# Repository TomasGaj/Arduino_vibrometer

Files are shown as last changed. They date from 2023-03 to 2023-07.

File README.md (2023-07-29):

# Arduino UNO contactless vibrometer

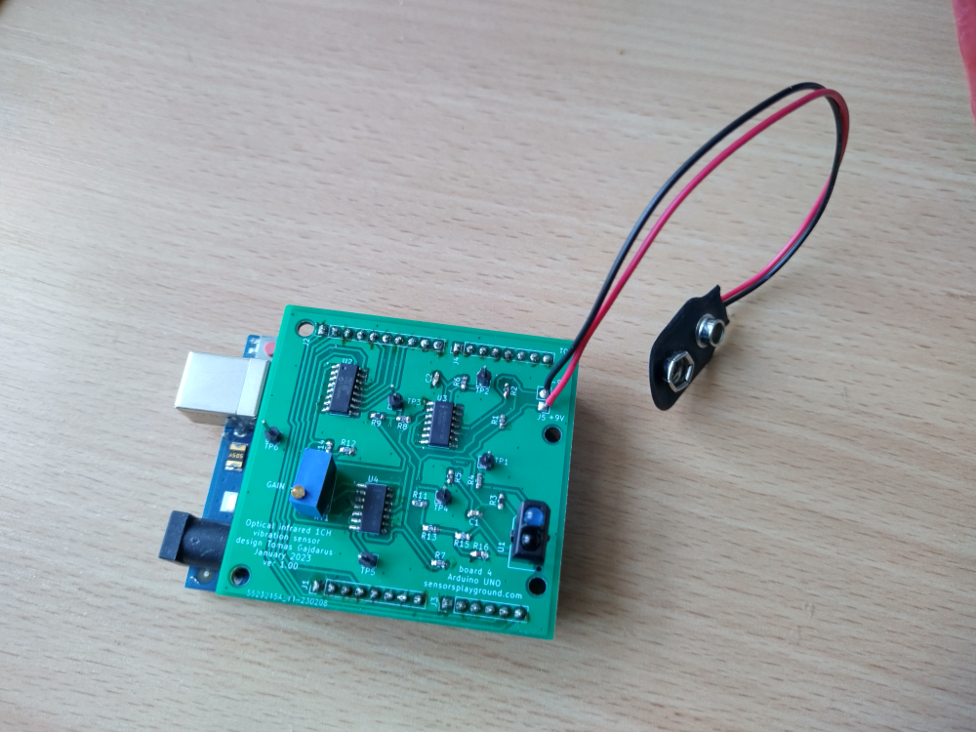
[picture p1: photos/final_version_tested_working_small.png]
final_version_tested_working_small


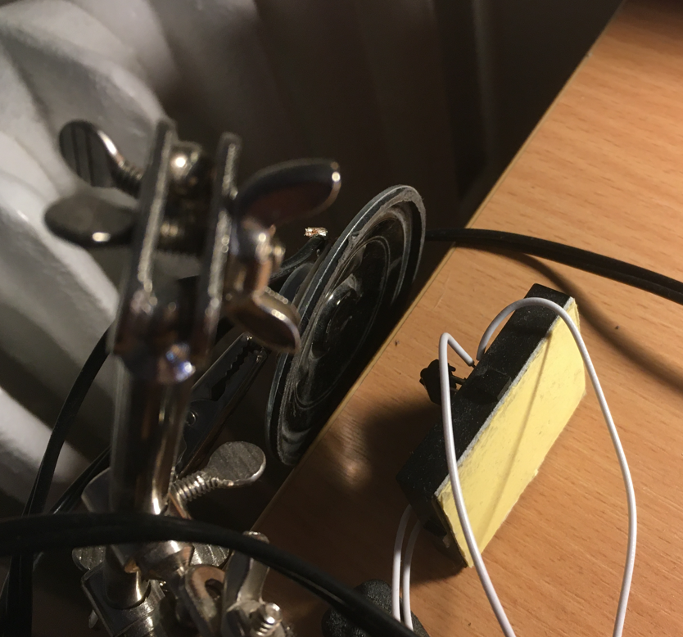
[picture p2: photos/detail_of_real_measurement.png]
detail of real measurement


**UPDATE 29-07-2023: I've squized Arduino and MPC3008 to the maximum, in the meanwhile
I didn't continue in C# as I optimized Arduino otput data format, see:** [Arduino_Nano_MPC3008_logger](https://github.com/TomasGaj/Arduino_Nano_MPC3008_logger)

## General Introduction

It's expansion board for Arduino UNO.
Vibrometer is based on TCRT5000 IR sensor and MCP3008 adc.
I used KiCAD 6.0.
It's tested and working.
Arduino is used only to send out ADC values together with time stamps.
C# application is coming.
Up to now I was not able to eliminate noise comping from USB supply (50 Hz), so I use 9V battery to supply power to the circuit.

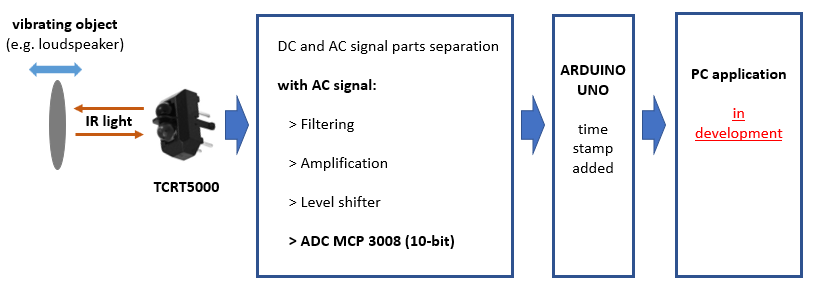
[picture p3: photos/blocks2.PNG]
blocks


## Physical principle

It's light intensity distance sensor. The closer the object is, the more light is reflected back to phototransistor.
However, the correct distance of vibrating object can not be measured without calibration. I hope I'll solve later.
Working distance is 15-25 mm.

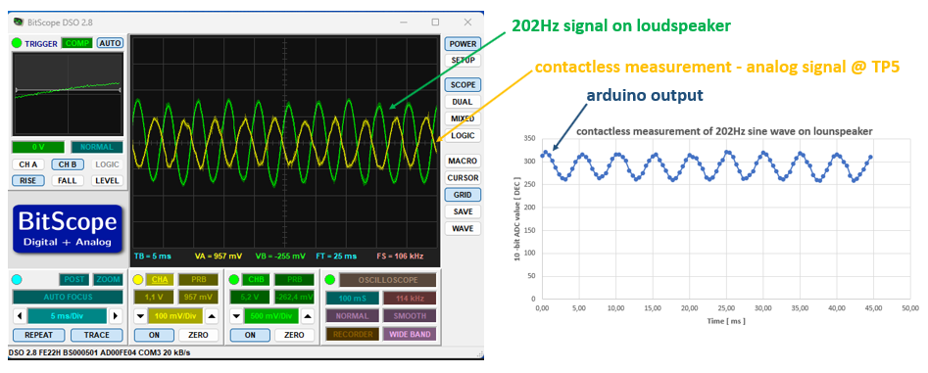
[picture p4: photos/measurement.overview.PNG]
measurement.overview


## Arduino code

I use this SW library:
[Fast MCP3008 library for Arduino Uno](https://github.com/arithmechanics/fast-MCP3008)

I modified the original code, I am sending out data in this format:

**ADC VALUE** (hex, 10-bit adc) ***(space)*** **MICRO-SECONDS** (hex, result of Arduino function ***micros()***)

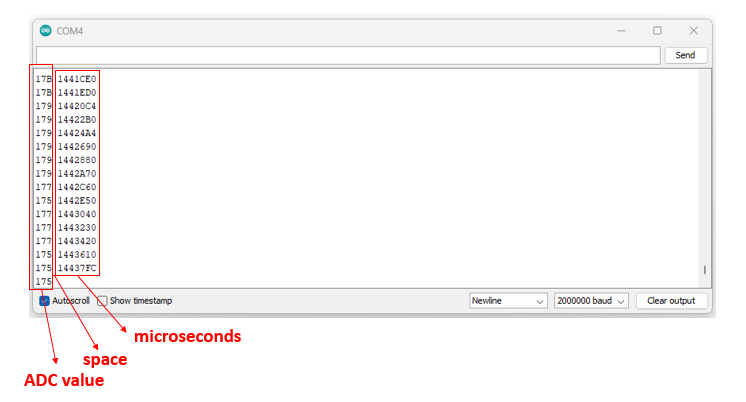
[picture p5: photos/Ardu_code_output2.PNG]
Arduino code output


## Electrical circuit
**Signal path:**

Signal -> High pass filter -> Low pass filter -> Amplifier -> Level shifter -> ADC (here MCP3008) -> Arduino Uno

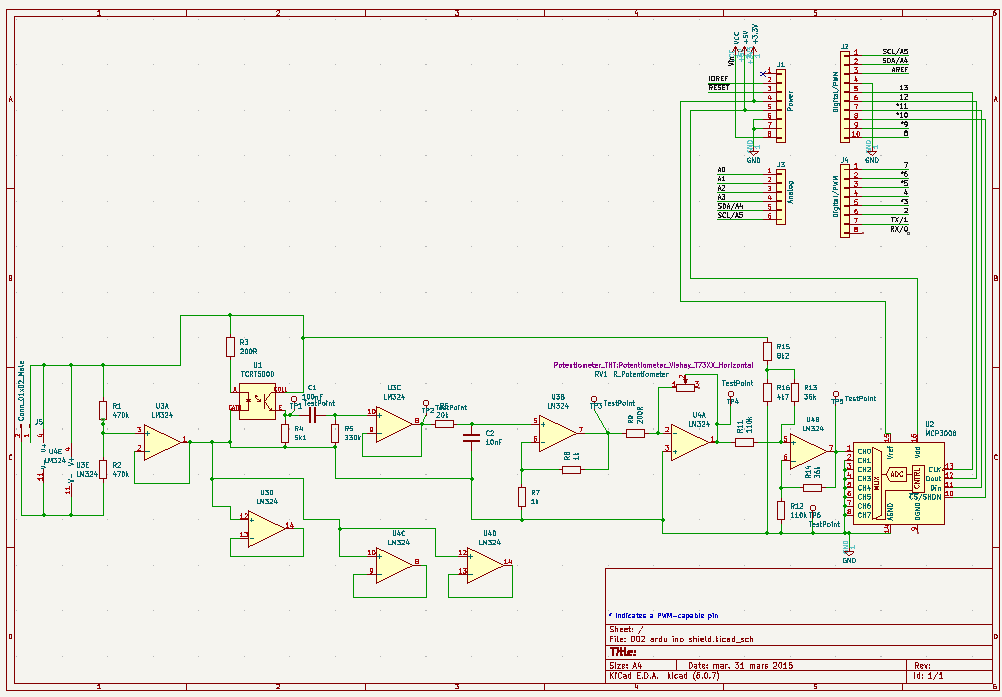
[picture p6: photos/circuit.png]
circuit


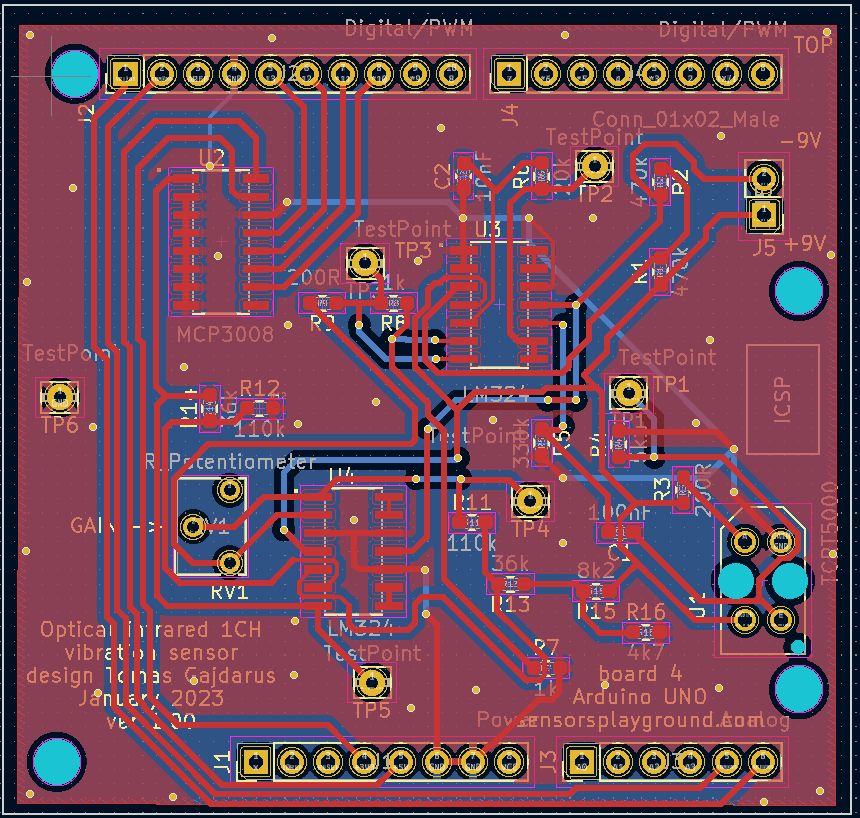
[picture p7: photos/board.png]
board


**My electrical design is inspired by:**

[Matiss Malahs - Design of a Low Cost Laser Vibrometer System](https://www.theseus.fi/handle/10024/89919)

[Heart Rate Measurement using PPG](http://www.ee.iitb.ac.in/~stallur/wp-content/uploads/2017/02/Heart-Rate-Measurement-using-PPG1.pdf)

## Details of the electrical circuit
I needed to do adjustments:
   - high pass filter is calculater fc = 4.82 Hz
   - high pass is also removing away DC part of the signal
   - low pass is calculated fc = 796 Hz
   - **everythnig above 200Hz looks ugly with actual data acqusition speed**
   - TestPoint 1 - direct output from phototransistor (proportional to light intensity)
   - TestPoint 2 - voltage after high pass filter
   - TestPoint 3 - voltage after low pass filter
   - TestPoint 4 - voltage after amplification
   - TestPoint 5 - signal before entering ADC
   - TestPoint 6 - ground
   
## Next steps

  - testing and testing...
  - speed up Arduino code
  - eliminate 9V battery
  - finish C# app
  - thinking about ARM processor (now testing RPi)
  - thinking about more complicated physical principle (planning intensity modulation tests, reading about self-mixing)
 
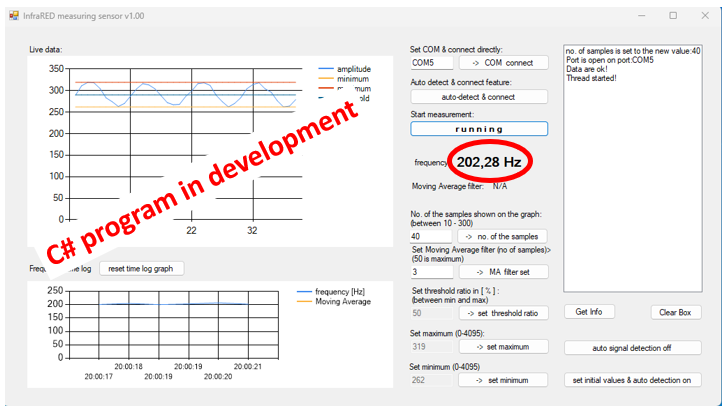
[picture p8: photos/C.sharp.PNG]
C#
 
 
**More about testing and other details:**

[sensorsplayground.com](http://www.sensorsplayground.com/)

Enjoy!

Tomas Gajdarus

tomas (dot) gajdarus (at) seznam (dot) cz

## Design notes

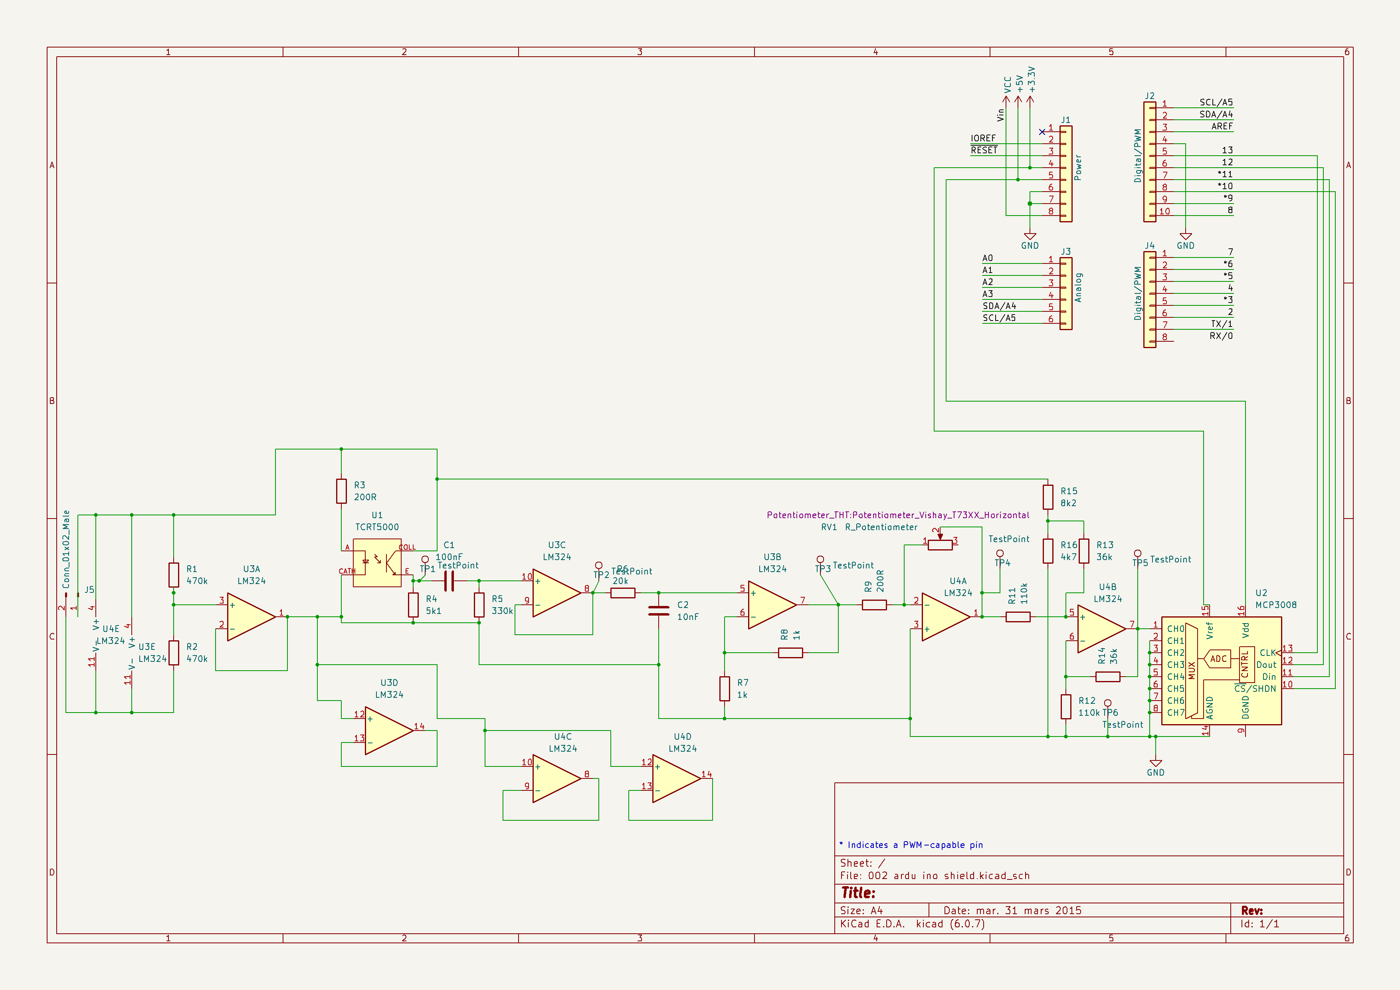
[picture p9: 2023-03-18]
Schematics and 3D view v1.0/Arduino_vibrometer_schematics_v 1.0.png

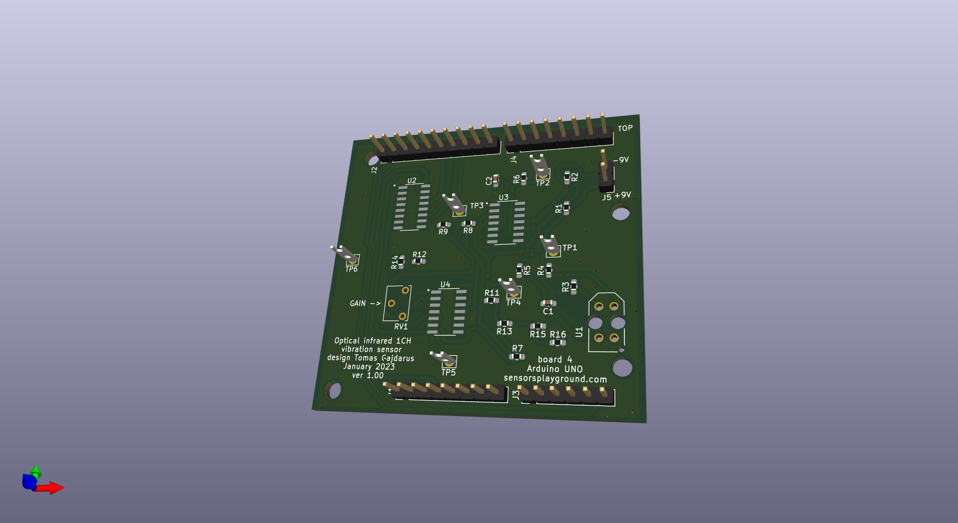
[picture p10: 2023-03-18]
Schematics and 3D view v1.0/3D_view_v1.0.jpg

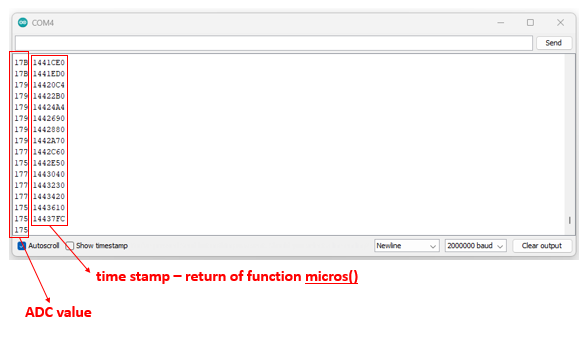
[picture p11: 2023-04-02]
photos/Ardu_code_output.PNG

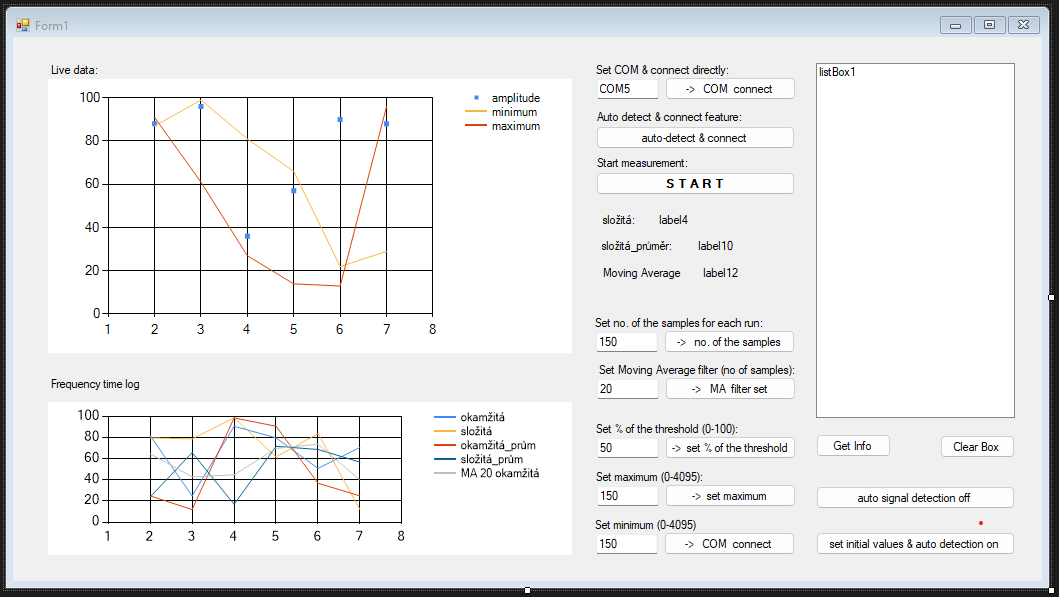
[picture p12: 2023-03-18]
photos/C# PC application (in development).png

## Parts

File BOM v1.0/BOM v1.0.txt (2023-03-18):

18.3.2023

created by Tomas Gajdarus

Note:in BOM is missing (I had components in-house):

	- 20k potenciometer
	- TCRT5000
	- 9V battery connector

FARNELL

1x MCP3008-I/SL 10BIT ADC, 8 CH, SPI, SMD, SOIC16
Order Code: 1292241 

2x LM324ADR OP AMP, QUAD LOW POWER, SMD, SOIC14
Order Code: 3117046

2x RC0603FR-07470KL RES, 470K, 1%, 0.1W, 0603, THICK FILM
Order Code: 9238808

2x CRCW0603200RFKEA RES, 200R, 1%, 0.1W, 0603, THICK FILM
Order Code: 1469777

1x MCWR06X5101FTL RES, 5K1, 1%, 0.1W, 0603, THICK FILM
Order Code: 2447404

1x CR0603-FX-3303ELF RES, 330K, 1%, 0603, THICK FILM
Order Code: 2908296 

1x RC0603FR-0720KL RES, 20K, 1%, 0.1W, 0603, THICK FILM
Order Code: 3495765

2x MCWR06X1001FTL RES, 1K, 1%, 0.1W, 0603, THICK FILM
Order Code: 2447272 

1x RC0603FR-0736KL RES, 36K, 1%, 0.1W, 0603, THICK FILM
Order Code: 3495824

1x MCWR06X8201FTL RES, 8K2, 1%, 0.1W, THICK FILM
Order Code: 2447442 

1x SFR03EZPF4701 RES, 4K7, 1%, 0603, THICK FILM
Order Code: 2887235

2x MCWR06X1103FTL RES, 110K, 1%, 0.1W, THICK FILM
Order Code: 2447234

1x 0603YC103KAT2A CAP, 0.01µF, 16V, 10%, X7R, 0603
Order Code: 2280661

1x 0603YC104JAT2A CAP, 0.1µF, 16V, 5%, X7R, 0603
Order Code: 1740612 

2x 2211S-22G CONNECTOR, HEADER, 22POS, 1ROW, 2.54MM
Order Code: 2847167

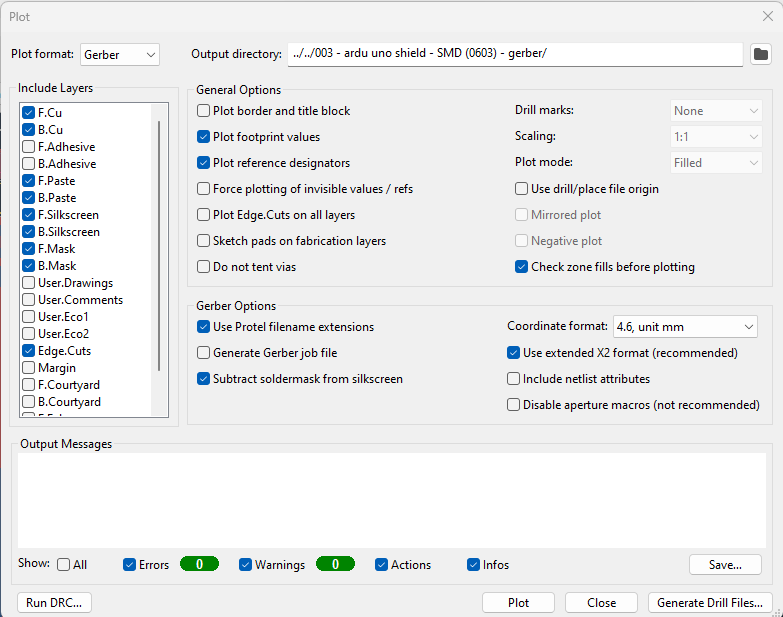
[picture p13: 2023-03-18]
Gerber files (ordered in JLCPCB, tested, working)/jak KiCAD 2023-02-08 082753.png

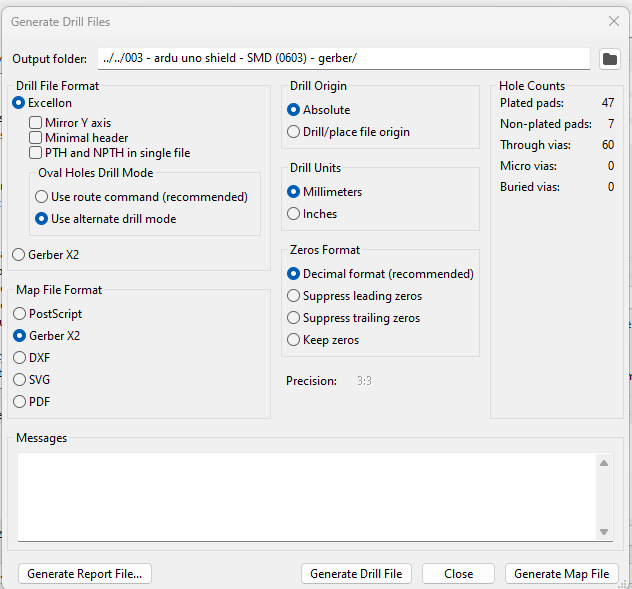
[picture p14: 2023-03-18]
Gerber files (ordered in JLCPCB, tested, working)/jak KiCAD2 2023-02-08 082753.png

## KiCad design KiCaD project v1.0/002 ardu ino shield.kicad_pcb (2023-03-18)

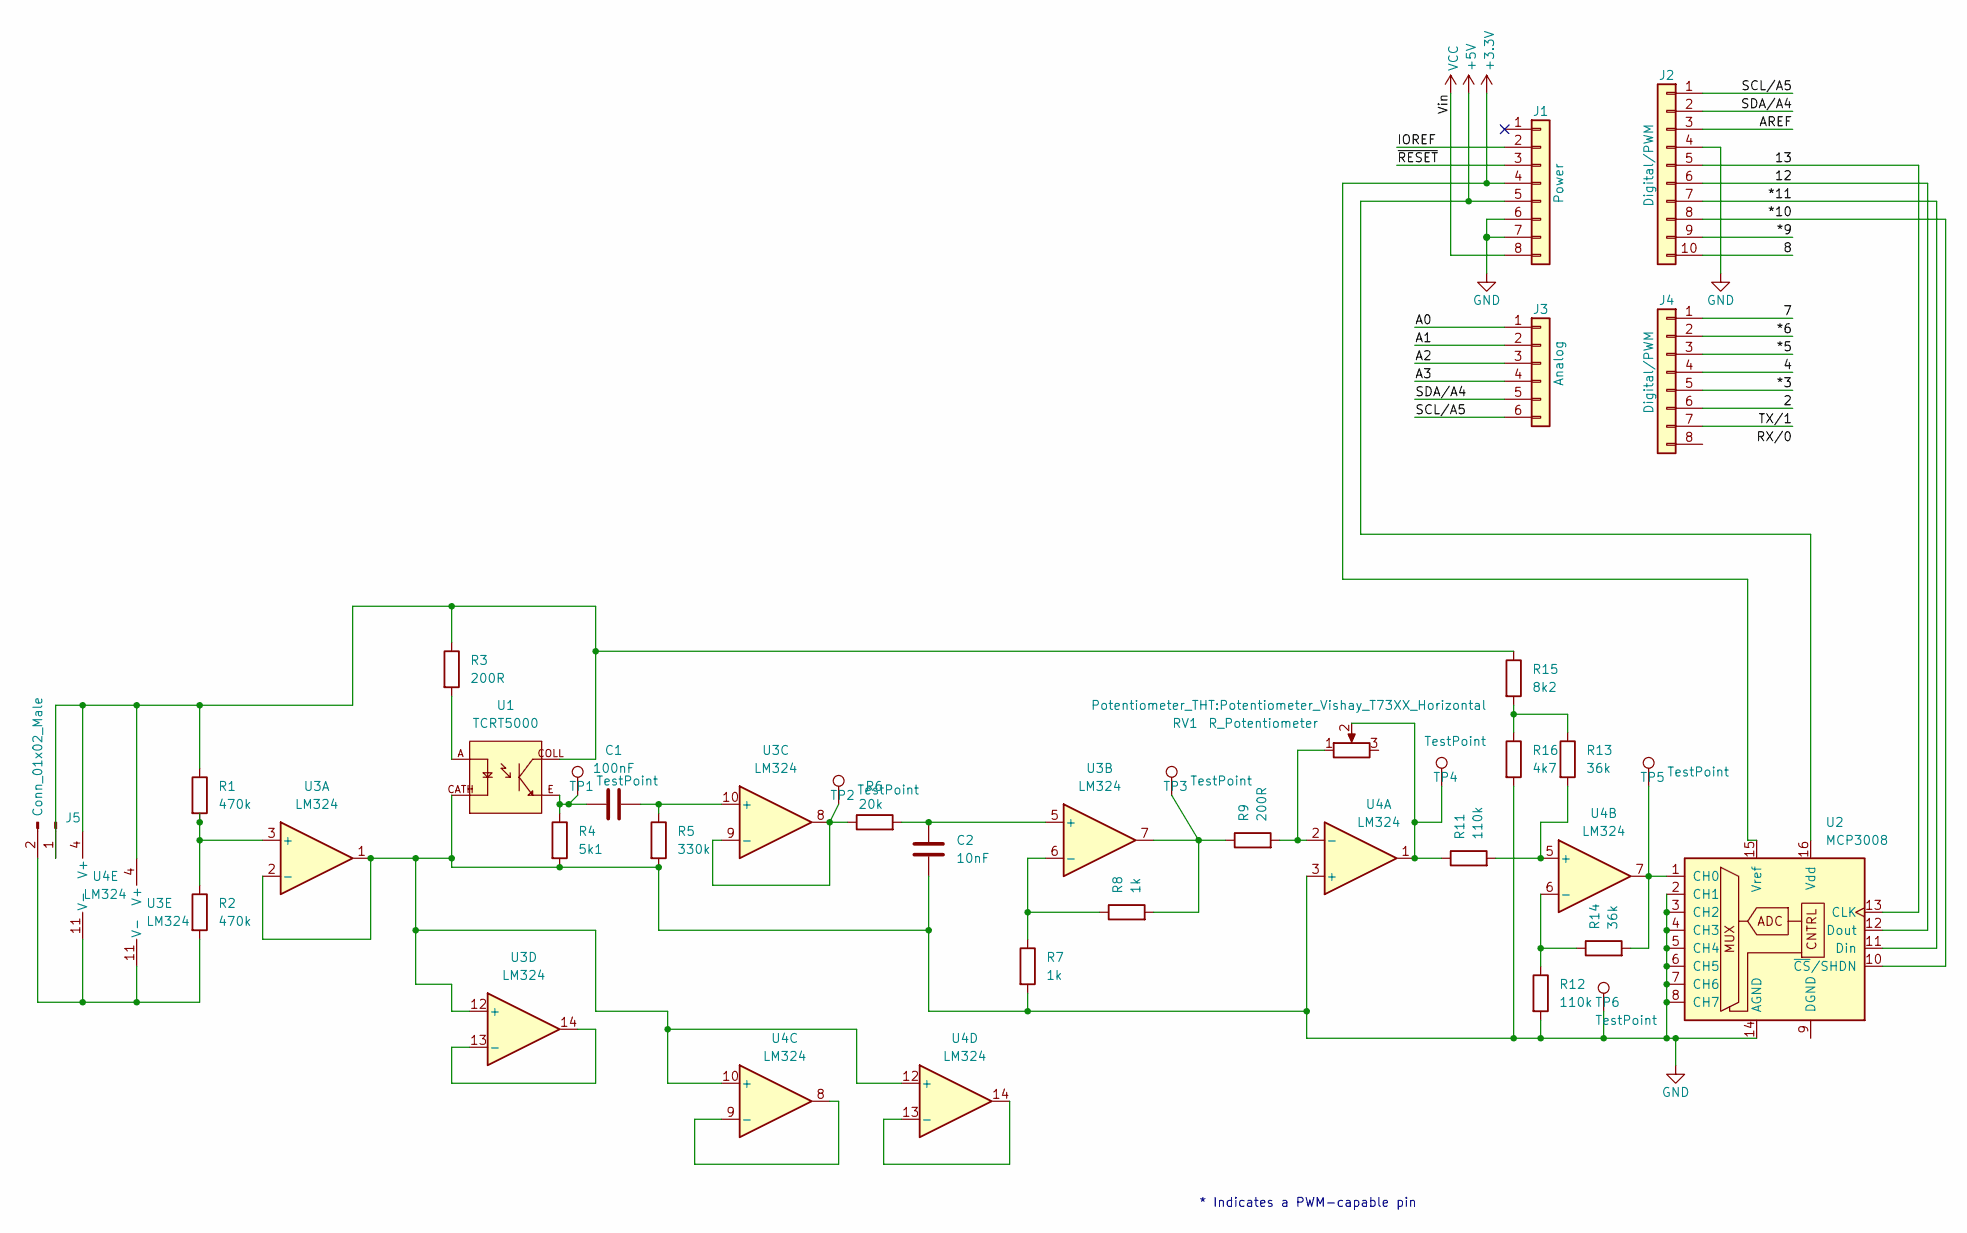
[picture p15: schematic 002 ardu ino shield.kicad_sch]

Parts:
C1: 100nF; C_0603_1608Metric_Pad1.08x0.95mm_HandSolder
C2: 10nF; C_0603_1608Metric_Pad1.08x0.95mm_HandSolder
J1: Power; PinHeader_1x08_P2.54mm_Vertical
J2: Digital/PWM; PinHeader_1x10_P2.54mm_Vertical
J3: Analog; PinHeader_1x06_P2.54mm_Vertical
J4: Digital/PWM; PinHeader_1x08_P2.54mm_Vertical
J5: Conn_01x02_Male; PinHeader_1x02_P2.54mm_Vertical
R1, R2: 470k; R_0603_1608Metric_Pad0.98x0.95mm_HandSolder
R3, R9: 200R; R_0603_1608Metric_Pad0.98x0.95mm_HandSolder
R4: 5k1; R_0603_1608Metric_Pad0.98x0.95mm_HandSolder
R5: 330k; R_0603_1608Metric_Pad0.98x0.95mm_HandSolder
R6: 20k; R_0603_1608Metric_Pad0.98x0.95mm_HandSolder
R7, R8: 1k; R_0603_1608Metric_Pad0.98x0.95mm_HandSolder
R11, R12: 110k; R_0603_1608Metric_Pad0.98x0.95mm_HandSolder
R13, R14: 36k; R_0603_1608Metric_Pad0.98x0.95mm_HandSolder
R15: 8k2; R_0603_1608Metric_Pad0.98x0.95mm_HandSolder
R16: 4k7; R_0603_1608Metric_Pad0.98x0.95mm_HandSolder
RV1: R_Potentiometer; Potentiometer_Vishay_T73XX_Horizontal
TP1, TP2, TP3, TP4, TP5, TP6: TestPoint; Pin_D0.9mm_L10.0mm_W2.4mm_FlatFork
U1: TCRT5000; OPTO_TCRT5000; PARTREV 1.7
U2: MCP3008; SOIC127P600X175-16N
U3, U4: LM324; SOIC127P600X175-14N

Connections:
+3V3: J1.4, U2.15 (Vref)
+5V: J1.5, U2.16 (Vdd)
/2: J4.6
/4: J4.4
/7: J4.1
/8: J2.10
/12: J2.6, U2.12 (Dout)
/13: J2.5, U2.13 (CLK)
/*3: J4.5
/*5: J4.3
/*6: J4.2
/*9: J2.9
/*10: J2.8, U2.10 (~CS/SHDN)
/*11: J2.7, U2.11 (Din)
/A0: J3.1
/A1: J3.2
/A2: J3.3
/A3: J3.4
/AREF: J2.3
/IOREF: J1.2
/SCL/A5: J2.1, J3.6
/SDA/A4: J2.2, J3.5
/TX/1: J4.7
/~RESET: J1.3
GND: C2.1, J1.6, J1.7, J2.4, R4.2, R5.2, R7.2, R12.2, R16.2, TP6.1, U1.CATH, U2.2 (CH1), U2.3 (CH2), U2.4 (CH3), U2.5 (CH4), U2.6 (CH5), U2.7 (CH6), U2.8 (CH7), U2.14 (AGND), U3.1, U3.2 (-), U3.12 (+), U4.3 (+), U4.10 (+), U4.12 (+)
unnamed: C1.1, R4.1, TP1.1, U1.E
unnamed: C1.2, R5.1, U3.10 (+)
unnamed: C2.2, R6.2, U3.5 (+)
unnamed: J5.1, R1.1, R3.1, R15.1, U1.COLL, U3.4 (V+), U4.4 (V+)
unnamed: J5.2, R2.2, U3.11 (V-), U4.11 (V-)
unnamed: R1.2, R2.1, U3.3 (+)
unnamed: R3.2, U1.A
unnamed: R6.1, TP2.1, U3.8, U3.9 (-)
unnamed: R7.1, R8.1, U3.6 (-)
unnamed: R8.2, R9.1, TP3.1, U3.7
unnamed: R9.2, RV1.1, U4.2 (-)
unnamed: R11.1, RV1.2, TP4.1, U4.1
unnamed: R11.2, R13.2, U4.5 (+)
unnamed: R12.1, R14.1, U4.6 (-)
unnamed: R13.1, R15.2, R16.1
unnamed: R14.2, TP5.1, U2.1 (CH0), U4.7
unnamed: U3.13 (-), U3.14
unnamed: U4.8, U4.9 (-)
unnamed: U4.13 (-), U4.14
VCC: J1.8

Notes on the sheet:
* Indicates a PWM-capable pin

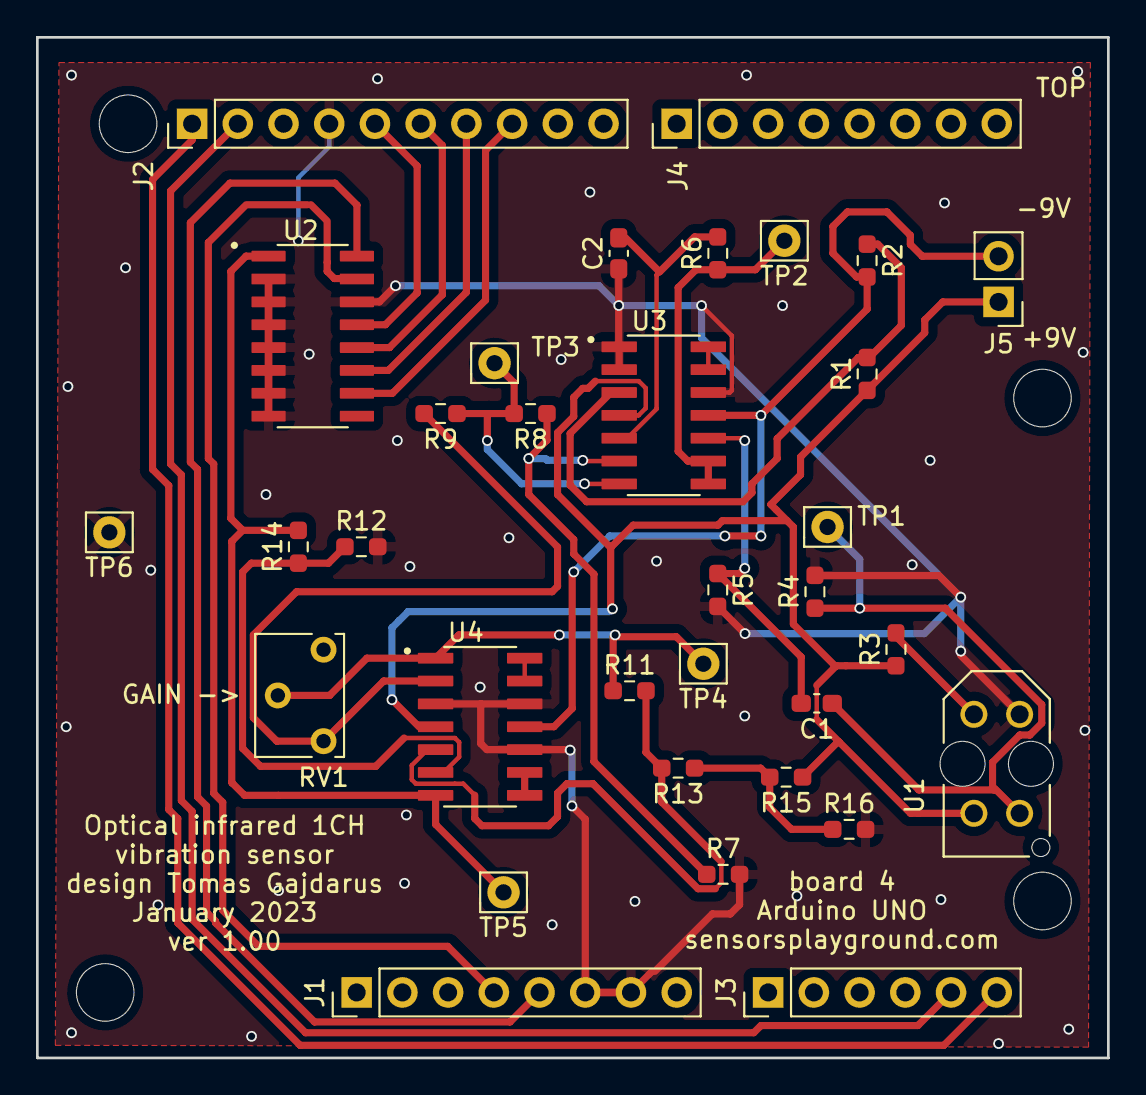
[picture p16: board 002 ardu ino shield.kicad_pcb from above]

Board: 2 copper layers, 59.5 x 56.7 mm, 37 parts (0 on the bottom side), 28 nets.

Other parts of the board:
MH1, MH2, MH3, MH4: MountingHole_3.2mm
